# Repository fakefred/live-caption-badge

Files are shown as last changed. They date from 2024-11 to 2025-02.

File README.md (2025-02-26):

# Live Caption Badge

The Live Caption Badge is my team's capstone project for EECS 473, from
September to December 2024. It is a device that transmits and transcribes
speech in a noisy environment in real-time for the hard of hearing.

For technical details, please read [our report](report.pdf) (10.6 MiB).

## Technical Highlights

- ESP32 with ESP-IDF and ESP-ADF
- FreeRTOS
- Audio streaming over HTTP
- Peer discovery over BLE
- Real-time speech-to-text with Vosk
- E-Paper over SPI
- Audio over I2S

## Files

- `firmware` is the firmware our product actually ran on Design Expo.
- `audio`, `BLEnWifi`, `echo`, `epaper` contain the code we used to test
  various components.
- `pcb` is our PCB design. It is a 4-layer board.
- `transcribe` contains the code for the central server `server_esp.py`,
  which ran on a laptop on Design Expo. It is responsible for transcribing
  text and relaying audio. We also used `hack.py` to apply hotfixes to the
  badges.

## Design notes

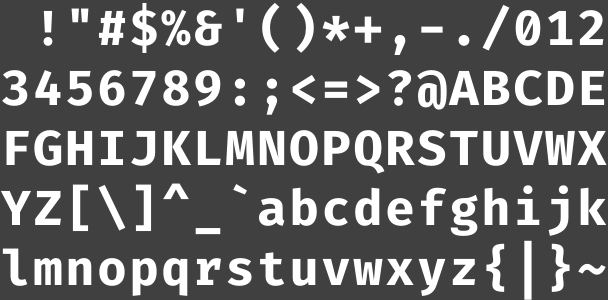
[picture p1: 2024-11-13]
epaper/tools/firacode48.png

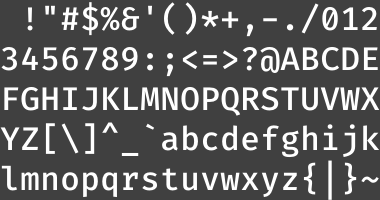
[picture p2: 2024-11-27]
epaper/tools/firacode32.png

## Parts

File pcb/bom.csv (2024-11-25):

Reference | Value | Qty
BT1 |  | 1
C1 | 100uF | 1
C2 | 22uF | 1
C3,C14,C15,C33,C34,C35 | 0.1uF | 6
C4,C5,C11-C13,C16-C21,C24-C32,C38-C40,C45 | 1uF | 24
C6 | 47uF | 1
C7-C10,C37,C41-C44,C46 | 10uF | 10
C22,C23,C48 | 22pF | 3
C36 | NC | 1
C47 | 4.7uF | 1
D1 | LED | 1
D2,D3,D4 | MBR0530 | 3
J1 | FPC24 | 1
J2 | Conn_01x06 | 1
J4 | AudioJack4 | 1
J5 | USB_C_Receptacle_USB2.0_16P | 1
L1 | 68uH | 1
Q1 | Si1308EDL | 1
Q2,Q3 | SS8050 | 2
R1,R7,R18,R19 | 10k | 4
R2,R3 | 3.3k | 2
R4,R5,R6 | 5.1k | 3
R8,R13,R14 | 0 | 3
R9 | 51 | 1
R10 | 2.2k | 1
R11,R12,R15 | 150k | 3
R16 | 300k | 1
R17 | 0.47 | 1
SW1 | SW_DPDT_x2 | 1
SW2 | RST | 1
SW3,SW4,SW5 | BTN | 3
SW6 | FLASH | 1
TP1-TP17 | TestPoint | 17
U1 | ESP32-S3-WROOM-1 | 1
U2,U3 | HE9073A33M5R | 2
U4 | ES7210 | 1
U5 | ES8311 | 1
U6 | IS31AP2005 | 1

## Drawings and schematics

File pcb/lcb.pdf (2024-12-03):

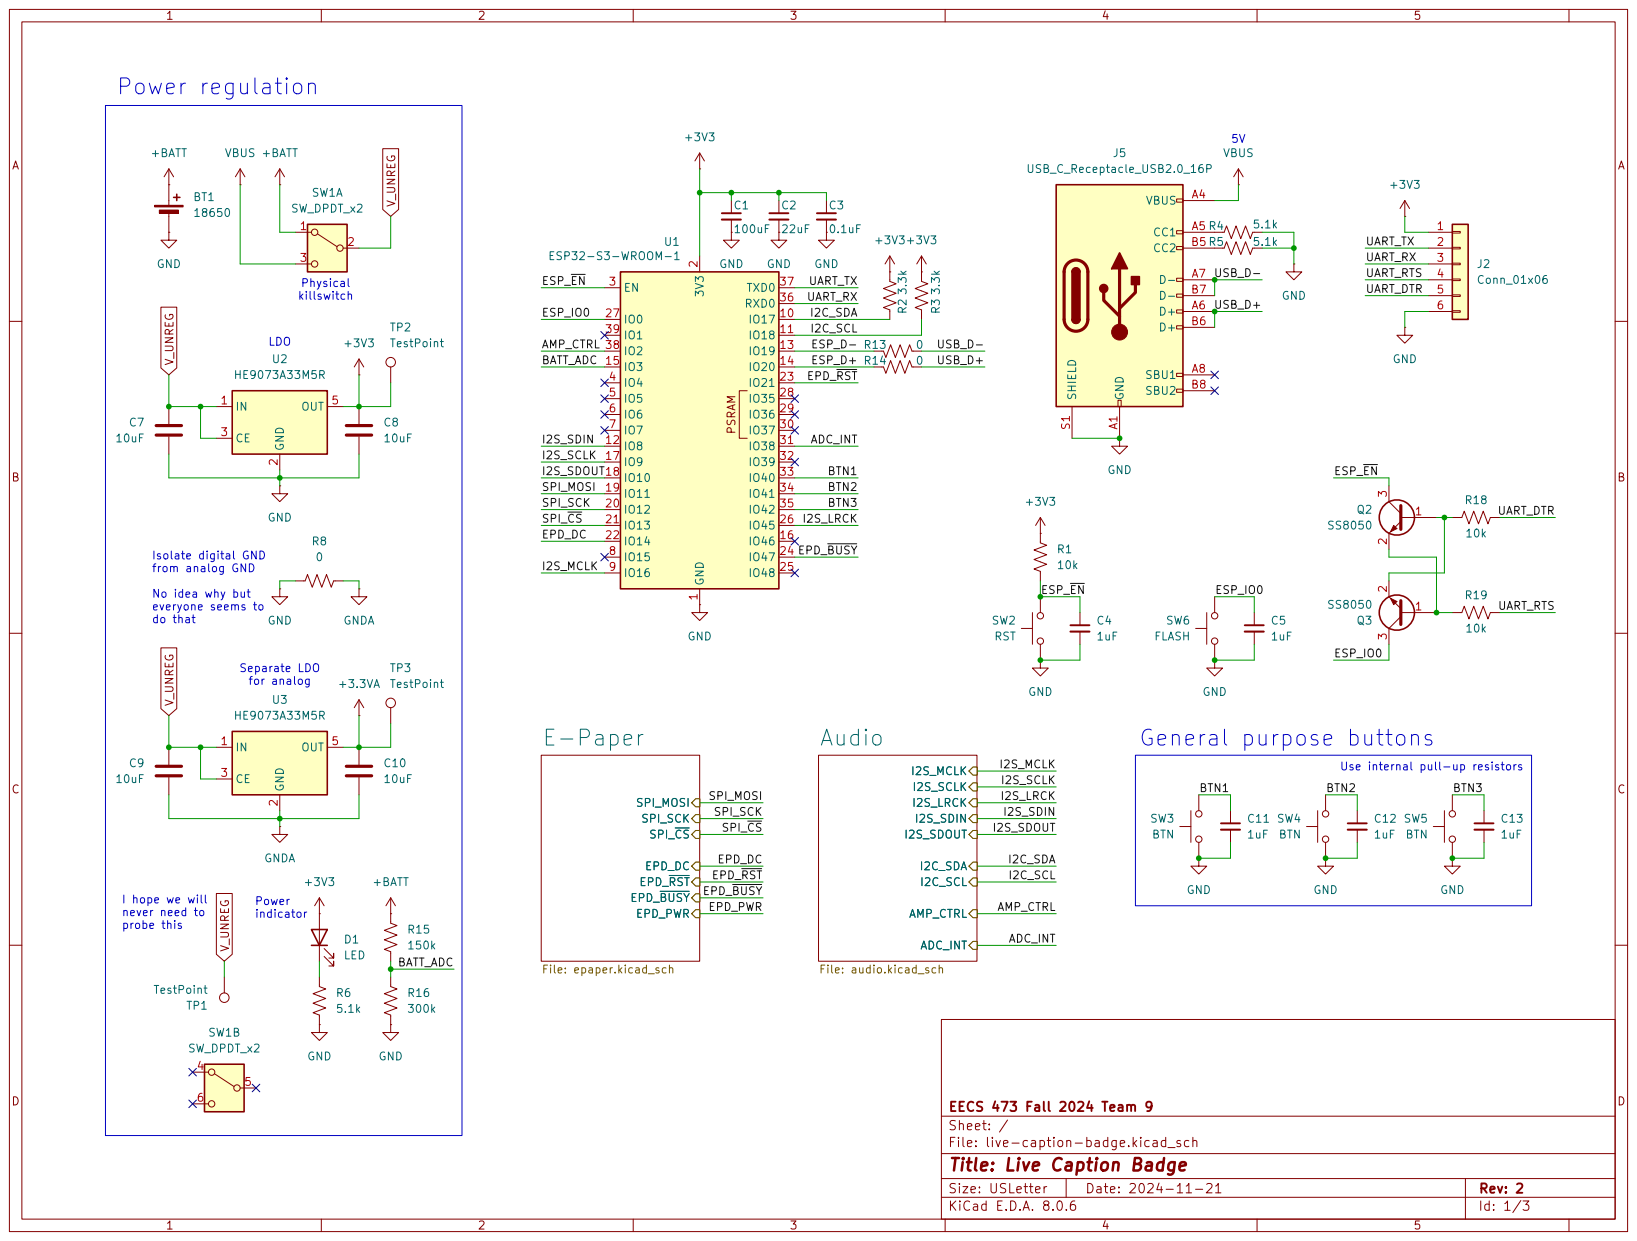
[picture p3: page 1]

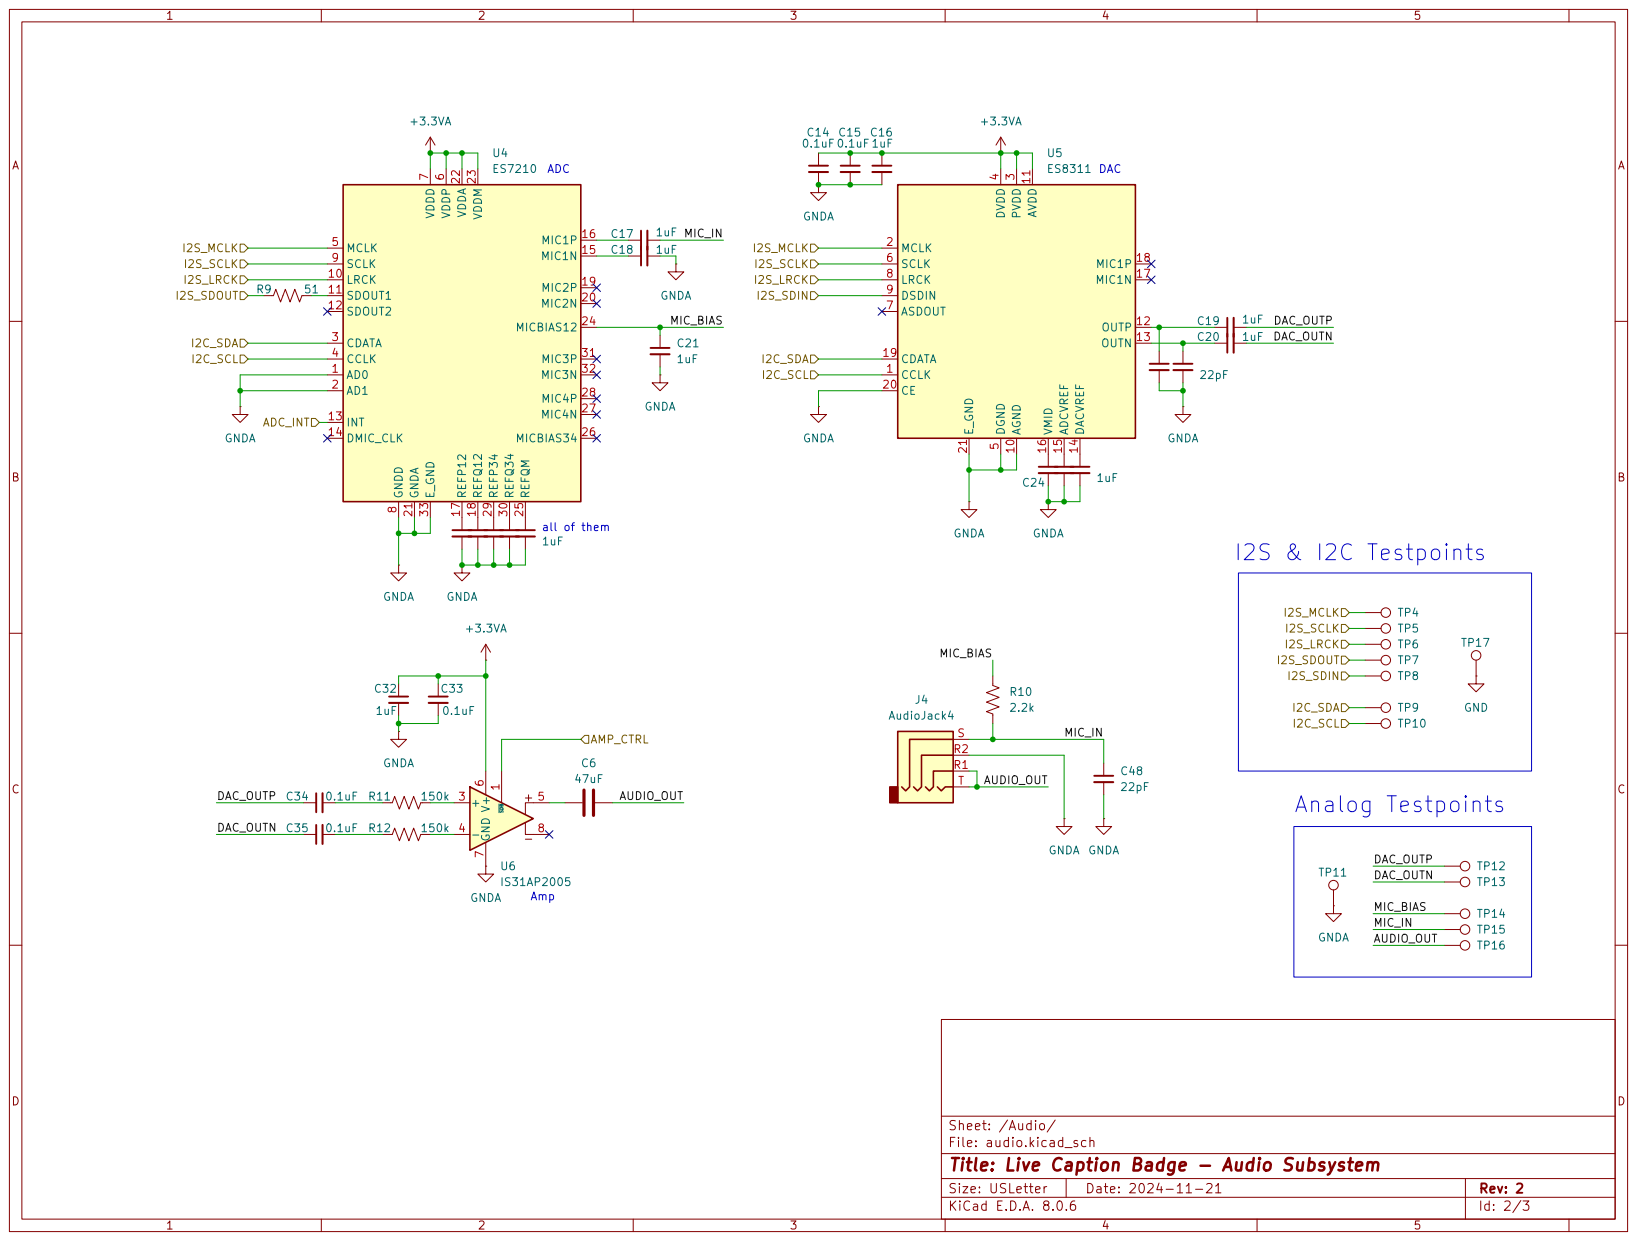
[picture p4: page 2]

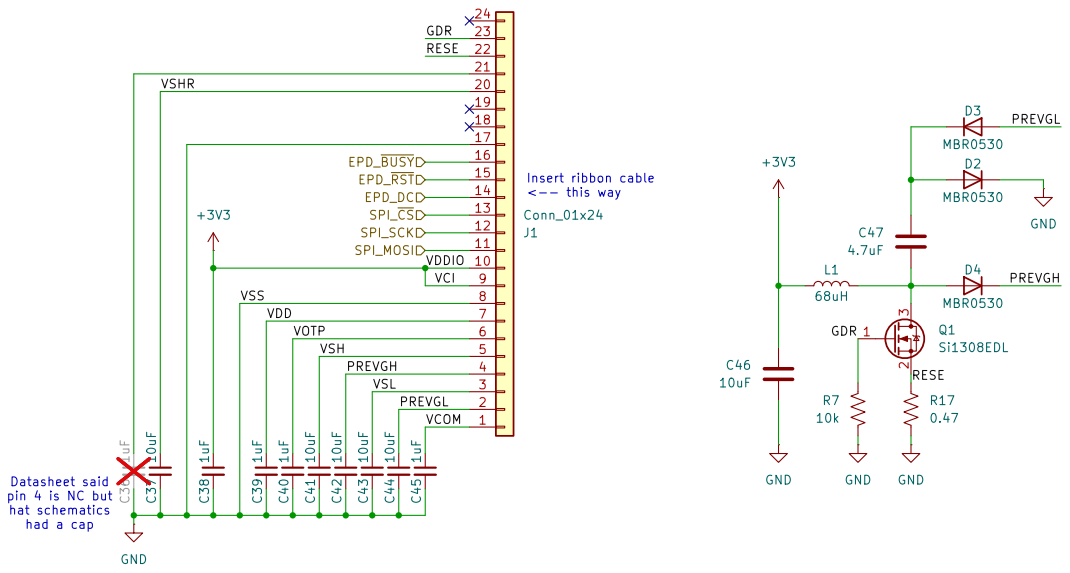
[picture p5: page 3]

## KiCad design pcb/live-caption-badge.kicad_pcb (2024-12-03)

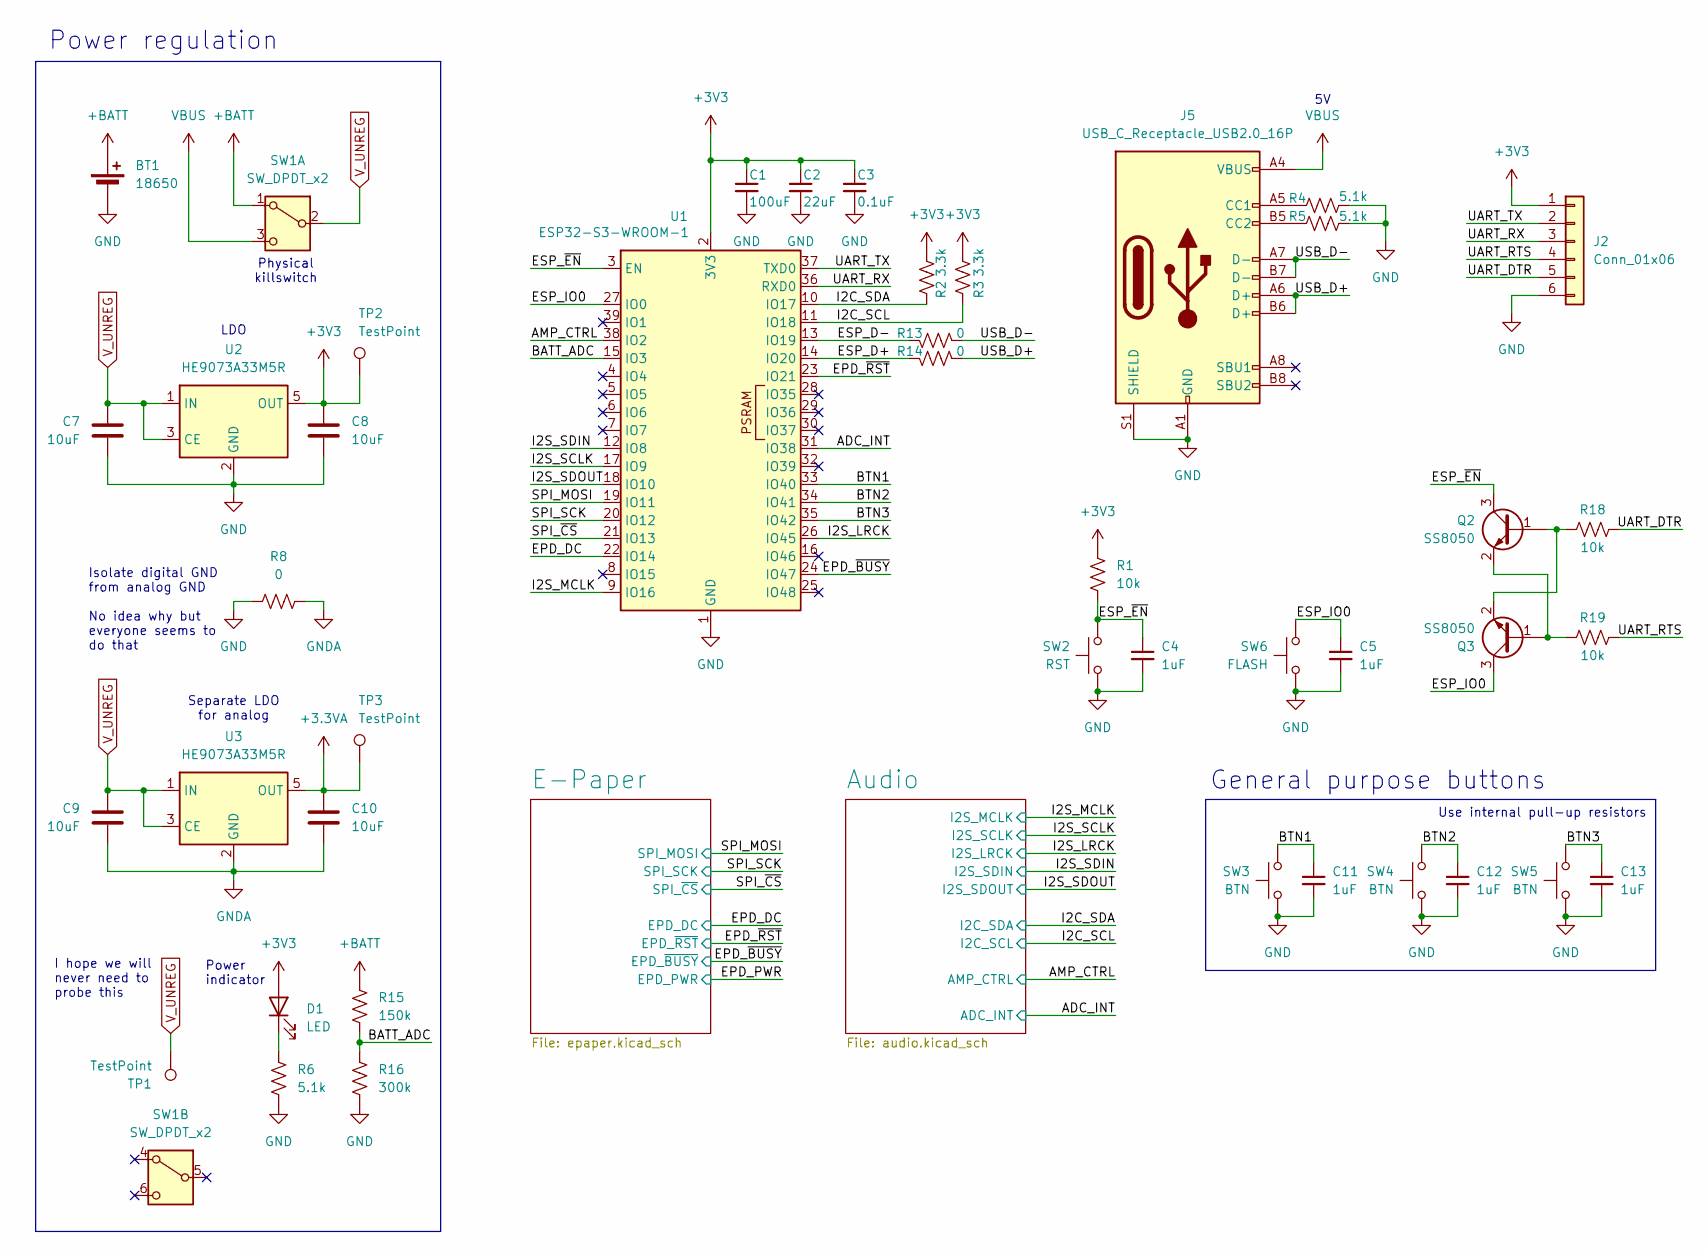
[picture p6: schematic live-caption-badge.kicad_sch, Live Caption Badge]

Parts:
BT1: 18650; BH-18650-B1BA002
C1: 100uF; CP_Radial_D8.0mm_P3.50mm
C2: 22uF; C_0603_1608Metric
C3: 0.1uF; C_0603_1608Metric
C4, C5, C11, C12, C13: 1uF; C_0603_1608Metric
C7, C8, C9, C10: 10uF; C_0603_1608Metric
D1: LED; LED_0603_1608Metric
J2: Conn_01x06; PinHeader_1x06_P2.54mm_Vertical
J5: USB_C_Receptacle_USB2.0_16P; USB_C_Receptacle_Molex_2169900002
Q2, Q3: SS8050; SOT-23
R1, R18, R19: 10k; R_0603_1608Metric
R2, R3: 3.3k; R_0603_1608Metric
R4, R5, R6: 5.1k; R_0603_1608Metric
R8, R13, R14: 0; R_0603_1608Metric
R15: 150k; R_0603_1608Metric
R16: 300k; R_0603_1608Metric
SW1: SW_DPDT_x2; SW_DPDT_SLW-867569-4A-N-D
SW2: RST; SW_Push_6x3mm
SW3, SW4, SW5: BTN; SW_Push_TL1100CF160Q
SW6: FLASH; SW_Push_6x3mm
TP1, TP2, TP3: TestPoint; PinHeader_1x01_P2.54mm_Vertical
U1: ESP32-S3-WROOM-1; ESP32-S3-WROOM-1-LargerVias
U2, U3: HE9073A33M5R; SOT-23-5

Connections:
+3.3VA: C10.1, TP3.1, U3.5 (OUT); also elsewhere on the board
+3V3: C1.1, C2.1, C3.1, C8.1, D1.2 (A), J2.1, R1.1, R2.1, R3.1, TP2.1, U1.2 (3V3), U2.5 (OUT); also elsewhere on the board
+BATT: BT1.1 (+), R15.2, SW1.1 (A)
/ADC_INT: U1.31 (IO38); also elsewhere on the board
/AMP_CTRL: U1.38 (IO2); also elsewhere on the board
/BATT_ADC: R15.1, R16.2, U1.15 (IO3)
/BTN1: C11.1, SW3.2, U1.33 (IO40)
/BTN2: C12.1, SW4.2, U1.34 (IO41)
/BTN3: C13.1, SW5.2, U1.35 (IO42)
/EPD_DC: U1.22 (IO14); also elsewhere on the board
/EPD_~BUSY: U1.24 (IO47); also elsewhere on the board
/EPD_~RST: U1.23 (IO21); also elsewhere on the board
/ESP_D+: R14.2, U1.14 (IO20)
/ESP_D-: R13.2, U1.13 (IO19)
/ESP_IO0: C5.1, Q3.3 (C), SW6.2, U1.27 (IO0)
/ESP_~EN: C4.1, Q2.3 (C), R1.2, SW2.2, U1.3 (EN)
/I2C_SCL: R3.2, U1.11 (IO18); also elsewhere on the board
/I2C_SDA: R2.2, U1.10 (IO17); also elsewhere on the board
/I2S_LRCK: U1.26 (IO45); also elsewhere on the board
/I2S_MCLK: U1.9 (IO16); also elsewhere on the board
/I2S_SCLK: U1.17 (IO9); also elsewhere on the board
/I2S_SDIN: U1.12 (IO8); also elsewhere on the board
/I2S_SDOUT: U1.18 (IO10); also elsewhere on the board
/SPI_MOSI: U1.19 (IO11); also elsewhere on the board
/SPI_SCK: U1.20 (IO12); also elsewhere on the board
/SPI_~CS: U1.21 (IO13); also elsewhere on the board
/UART_DTR: J2.5, R18.2
/UART_RTS: J2.4, R19.2
/UART_RX: J2.3, U1.36 (RXD0)
/UART_TX: J2.2, U1.37 (TXD0)
/USB_D+: J5.A6 (D+), J5.B6 (D+), R14.1
/USB_D-: J5.A7 (D-), J5.B7 (D-), R13.1
GND: BT1.2 (-), C1.2, C2.2, C3.2, C4.2, C5.2, C7.2, C8.2, C11.2, C12.2, C13.2, J2.6, J5.A1 (GND), J5.A12 (GND), J5.B1 (GND), J5.B12 (GND), J5.S1 (SHIELD), R4.2, R5.2, R6.1, R8.1, R16.1, SW2.1, SW3.1, SW4.1, SW5.1, SW6.1, U1.1 (GND), U1.40 (GND), U1.41 (GND), U2.2 (GND); also elsewhere on the board
GNDA: C9.2, C10.2, R8.2, U3.2 (GND); also elsewhere on the board
unnamed: D1.1 (K), R6.2
unnamed: J5.A5 (CC1), R4.1
unnamed: J5.B5 (CC2), R5.1
unnamed: Q2.1 (B), Q3.2 (E), R18.1
unnamed: Q2.2 (E), Q3.1 (B), R19.1
VBUS: J5.A4 (VBUS), J5.A9 (VBUS), J5.B4 (VBUS), J5.B9 (VBUS), SW1.3 (C)
V_UNREG: C7.1, C9.1, SW1.2 (B), TP1.1, U2.1 (IN), U2.3 (CE), U3.1 (IN), U3.3 (CE)

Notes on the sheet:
Power regulation
Physical killswitch
LDO
I hope we will never need to probe this
Power indicator
Use internal pull-up resistors
General purpose buttons
Isolate digital GND from analog GND No idea why but everyone seems to do that
Separate LDO for analog

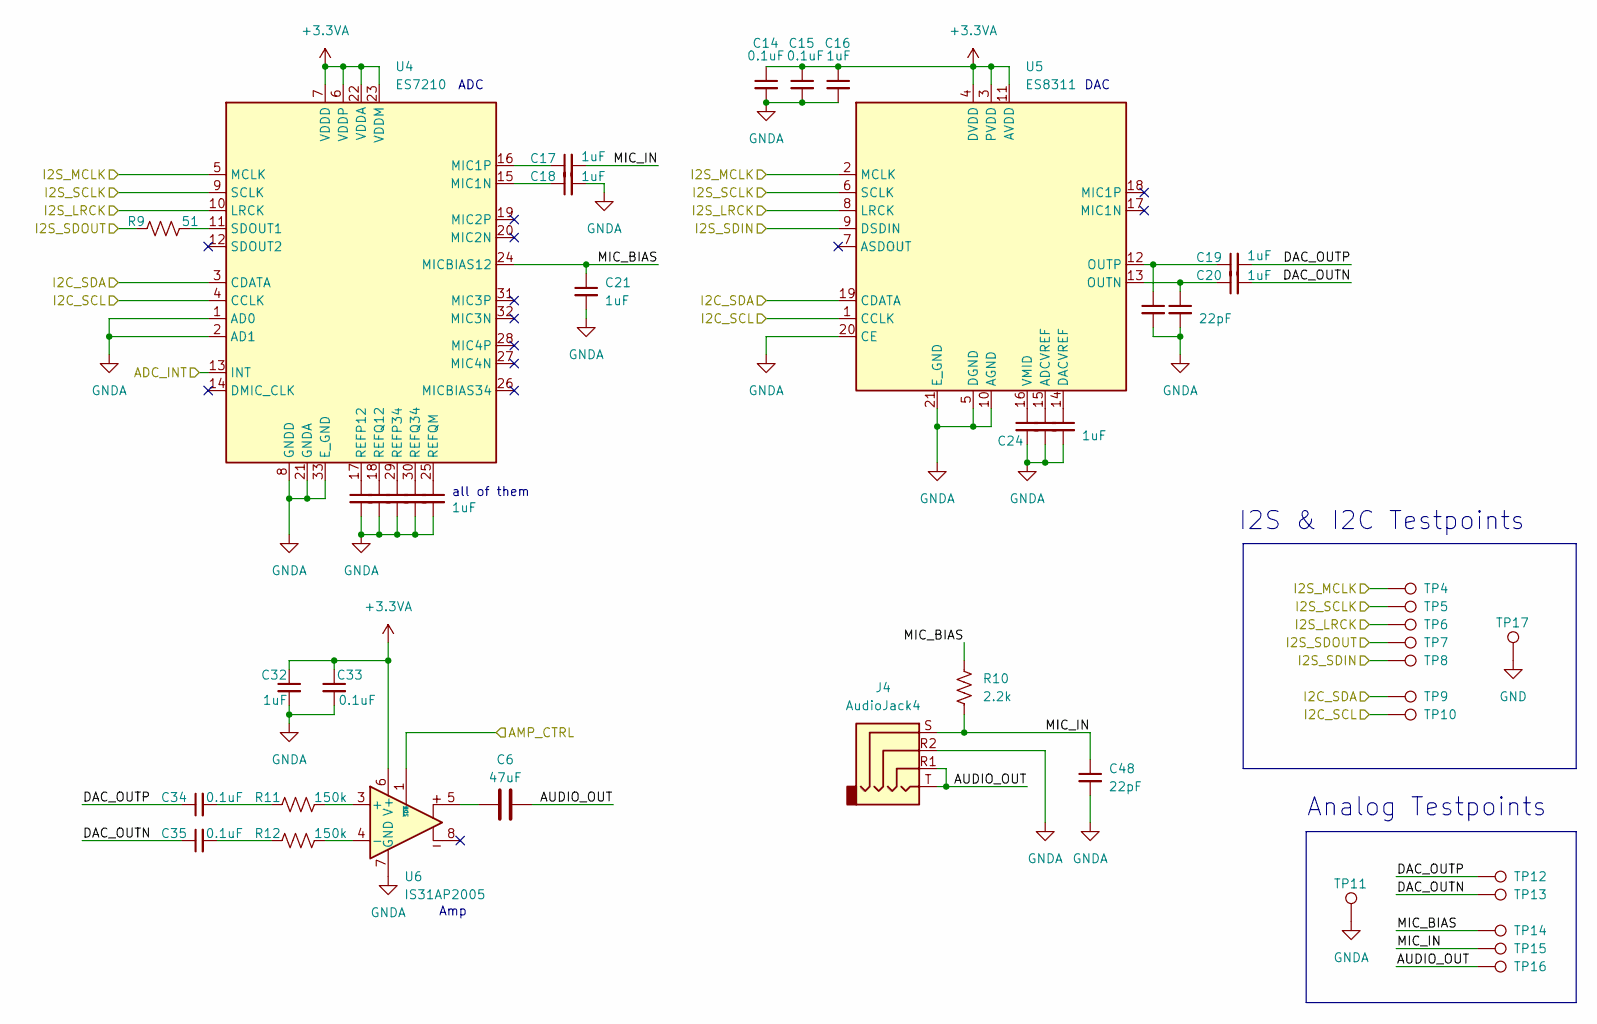
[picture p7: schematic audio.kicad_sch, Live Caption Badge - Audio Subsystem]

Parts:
C6: 47uF; C_0603_1608Metric
C14, C15, C33, C34, C35: 0.1uF; C_0603_1608Metric
C16, C17, C18, C19, C20, C21, C24, C25, C26, C27, C28, C29, C30, C31, C32: 1uF; C_0603_1608Metric
C22, C23, C48: 22pF; C_0603_1608Metric
J4: AudioJack4; Jack_3.5mm_PJ320D_Horizontal
R9: 51; R_0603_1608Metric
R10: 2.2k; R_0603_1608Metric
R11, R12: 150k; R_0603_1608Metric
TP4, TP5, TP6, TP7, TP8, TP9, TP10, TP11, TP12, TP13, TP14, TP15, TP16, TP17: TestPoint; PinHeader_1x01_P2.54mm_Vertical
U4: ES7210; QFN-32-1EP_4x4mm_P0.4mm_EP2.9x2.9mm
U5: ES8311; QFN-20-1EP_3x3mm_P0.4mm_EP1.65x1.65mm
U6: IS31AP2005; MSOP-8_3x3mm_P0.65mm

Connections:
+3.3VA: C14.1, C15.1, C16.1, C32.1, C33.1, U4.6 (VDDP), U4.7 (VDDD), U4.22 (VDDA), U4.23 (VDDM), U5.3 (PVDD), U5.4 (DVDD), U5.11 (AVDD), U6.6 (V+); also elsewhere on the board
/ADC_INT: U4.13 (INT); also elsewhere on the board
/AMP_CTRL: U6.1 (~SDB); also elsewhere on the board
/Audio/AUDIO_OUT: C6.2, J4.R1, J4.T, TP16.1
/Audio/DAC_OUTN: C20.2, C35.1, TP13.1
/Audio/DAC_OUTP: C19.2, C34.1, TP12.1
/Audio/MIC_BIAS: C21.1, R10.1, TP14.1, U4.24 (MICBIAS12)
/Audio/MIC_IN: C17.2, C48.1, J4.S, R10.2, TP15.1
/I2C_SCL: TP10.1, U4.4 (CCLK), U5.1 (CCLK); also elsewhere on the board
/I2C_SDA: TP9.1, U4.3 (CDATA), U5.19 (CDATA); also elsewhere on the board
/I2S_LRCK: TP6.1, U4.10 (LRCK), U5.8 (LRCK); also elsewhere on the board
/I2S_MCLK: TP4.1, U4.5 (MCLK), U5.2 (MCLK); also elsewhere on the board
/I2S_SCLK: TP5.1, U4.9 (SCLK), U5.6 (SCLK); also elsewhere on the board
/I2S_SDIN: TP8.1, U5.9 (DSDIN); also elsewhere on the board
/I2S_SDOUT: R9.1, TP7.1; also elsewhere on the board
GND: TP17.1; also elsewhere on the board
GNDA: C14.2, C15.2, C16.2, C18.2, C21.2, C22.2, C23.2, C24.2, C25.2, C26.2, C27.2, C28.2, C29.2, C30.2, C31.2, C32.2, C33.2, C48.2, J4.R2, TP11.1, U4.1 (AD0), U4.2 (AD1), U4.8 (GNDD), U4.21 (GNDA), U4.33 (E_GND), U5.5 (DGND), U5.10 (AGND), U5.20 (CE), U5.21 (E_GND), U6.7 (GND); also elsewhere on the board
unnamed: C6.1, U6.5
unnamed: C34.2, R11.1
unnamed: C35.2, R12.1
unnamed: C18.1, U4.15 (MIC1N)
unnamed: C17.1, U4.16 (MIC1P)
unnamed: C27.1, U4.17 (REFP12)
unnamed: C29.1, U4.29 (REFP34)
unnamed: C28.1, U4.18 (REFQ12)
unnamed: C30.1, U4.30 (REFQ34)
unnamed: C31.1, U4.25 (REFQM)
unnamed: R9.2, U4.11 (SDOUT1)
unnamed: C25.1, U5.15 (ADCVREF)
unnamed: C26.1, U5.14 (DACVREF)
unnamed: C20.1, C23.1, U5.13 (OUTN)
unnamed: C19.1, C22.1, U5.12 (OUTP)
unnamed: C24.1, U5.16 (VMID)
unnamed: R11.2, U6.3 (+)
unnamed: R12.2, U6.4 (-)

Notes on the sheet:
DAC
all of them
Amp
Analog Testpoints
I2S & I2C Testpoints
ADC

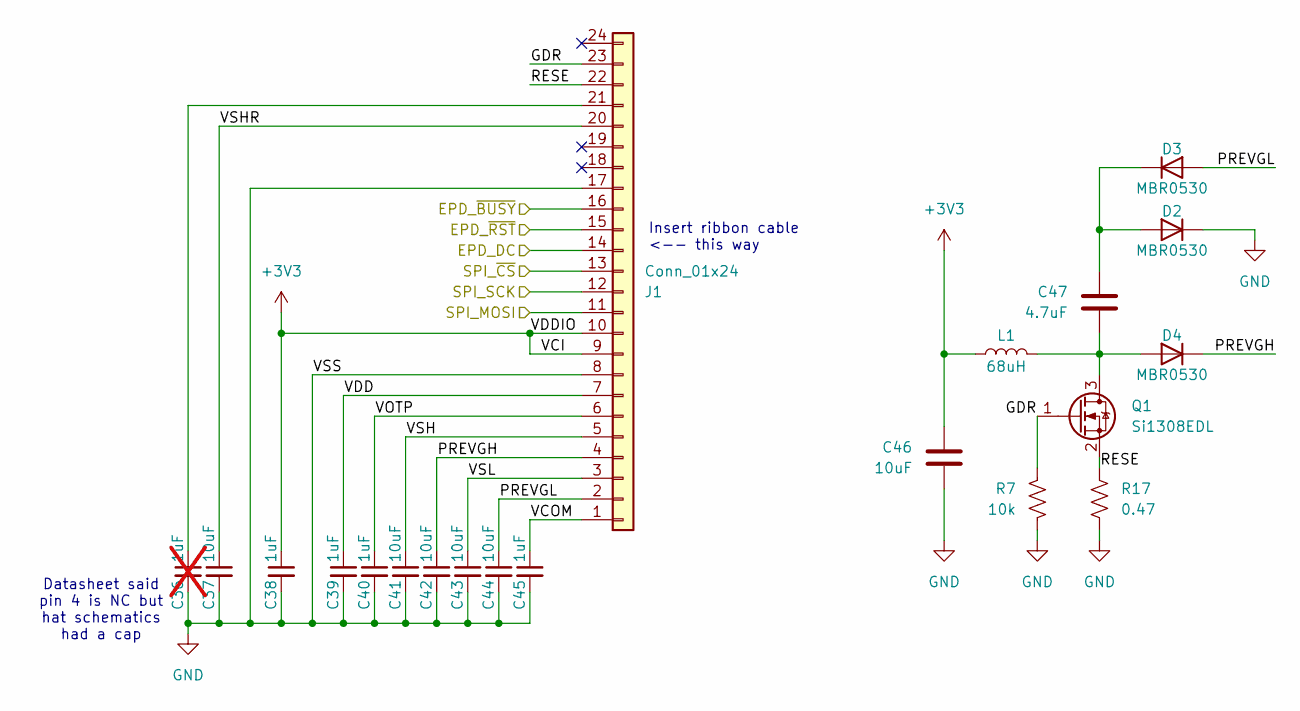
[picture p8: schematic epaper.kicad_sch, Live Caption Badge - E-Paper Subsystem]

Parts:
C36: 1uF; C_0603_1608Metric; not fitted
C37, C41, C42, C43, C44, C46: 10uF; C_0603_1608Metric
C38, C39, C40, C45: 1uF; C_0603_1608Metric
C47: 4.7uF; C_0603_1608Metric
D2, D3, D4: MBR0530; D_SOD-123
J1: Conn_01x24; FPC05024-13200_1x24-1MP_P0.50_Horizontal
L1: 68uH; L_Bourns-SDEE0406A
Q1: Si1308EDL; SOT-323_SC-70
R7: 10k; R_0603_1608Metric
R17: 0.47; R_0603_1608Metric

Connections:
+3V3: C38.1, C46.1, J1.9, J1.10, L1.1; also elsewhere on the board
/E-Paper/GDR: J1.23, Q1.1 (G), R7.1
/E-Paper/PREVGH: C42.1, D4.1 (K), J1.4
/E-Paper/PREVGL: C44.1, D3.2 (A), J1.2
/E-Paper/RESE: J1.22, Q1.2 (S), R17.1
/E-Paper/VCOM: C45.1, J1.1
/E-Paper/VDD: C39.1, J1.7
/E-Paper/VOTP: C40.1, J1.6
/E-Paper/VSH: C41.1, J1.5
/E-Paper/VSHR: C37.1, J1.20
/E-Paper/VSL: C43.1, J1.3
/EPD_DC: J1.14; also elsewhere on the board
/EPD_~BUSY: J1.16; also elsewhere on the board
/EPD_~RST: J1.15; also elsewhere on the board
/SPI_MOSI: J1.11; also elsewhere on the board
/SPI_SCK: J1.12; also elsewhere on the board
/SPI_~CS: J1.13; also elsewhere on the board
GND: C36.2, C37.2, C38.2, C39.2, C40.2, C41.2, C42.2, C43.2, C44.2, C45.2, C46.2, D2.1 (K), J1.8, J1.17, R7.2, R17.2; also elsewhere on the board
unnamed: C47.1, D2.2 (A), D3.1 (K)
unnamed: C47.2, D4.2 (A), L1.2, Q1.3 (D)
unnamed: C36.1, J1.21

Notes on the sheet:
Datasheet said pin 4 is NC but hat schematics had a cap
Insert ribbon cable <-- this way

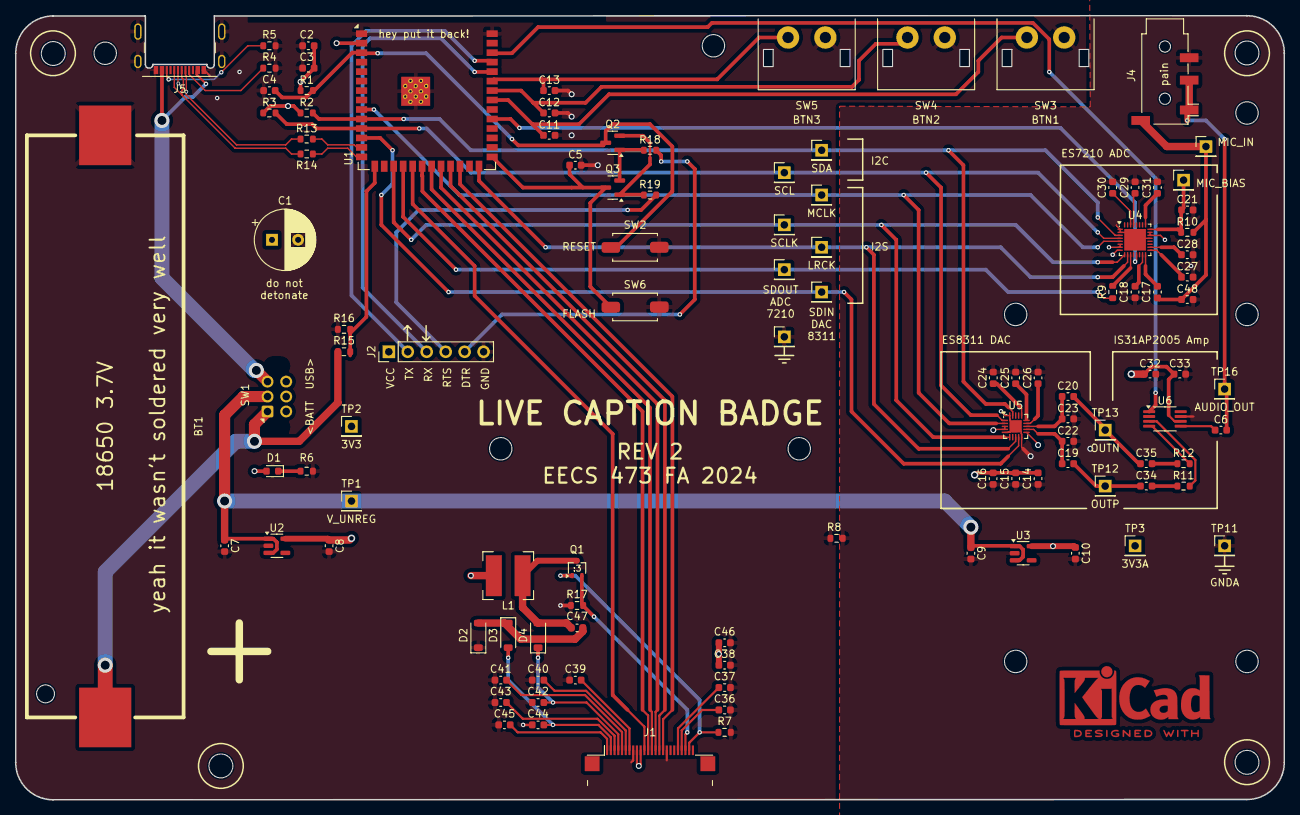
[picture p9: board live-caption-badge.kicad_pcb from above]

Board: 4 copper layers, 170.0 x 105.1 mm, 109 parts (0 on the bottom side), 77 nets.

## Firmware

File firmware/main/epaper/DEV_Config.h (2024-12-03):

/*****************************************************************************
* | File      	:   DEV_Config.h
* | Author      :   Waveshare team
* | Function    :   Hardware underlying interface
* | Info        :
*----------------
* |	This version:   V1.0
* | Date        :   2020-02-19
* | Info        :
#
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
******************************************************************************/
#ifndef _DEV_CONFIG_H_
#define _DEV_CONFIG_H_

#include "driver/gpio.h"
#include "freertos/FreeRTOS.h"
#include "SPI.h"
#include <stdint.h>
#include <stdio.h>

/**
 * data
 **/
#define UBYTE uint8_t
#define UWORD uint16_t
#define UDOUBLE uint32_t

/**
 * GPIO config
 **/
#define EPD_SCK_PIN GPIO_NUM_12
#define EPD_MOSI_PIN GPIO_NUM_11
#define EPD_MISO_PIN GPIO_NUM_48 // unused
#define EPD_CS_PIN GPIO_NUM_13
#define EPD_RST_PIN GPIO_NUM_21
#define EPD_DC_PIN GPIO_NUM_14
#define EPD_BUSY_PIN GPIO_NUM_47
#define EPD_PWR_PIN GPIO_NUM_7

#define GPIO_PIN_SET 1
#define GPIO_PIN_RESET 0

#define HIGH 1
#define LOW 0

/**
 * GPIO read and write
 **/
#define DEV_Digital_Write(_pin, _value) gpio_set_level(_pin, _value)
#define DEV_Digital_Read(_pin) gpio_get_level(_pin)

/**
 * delay x ms
 **/
#define DEV_Delay_ms(__xms) vTaskDelay(pdMS_TO_TICKS(__xms))

/*------------------------------------------------------------------------------------------------------*/
UBYTE DEV_Module_Init(void);
void  GPIO_Mode(UWORD GPIO_Pin, UWORD Mode);
void  DEV_SPI_WriteByte(UBYTE data);
UBYTE DEV_SPI_ReadByte();
void  DEV_SPI_Write_nByte(UBYTE *pData, UDOUBLE len);

#endif

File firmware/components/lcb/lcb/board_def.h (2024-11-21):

/*
 * ESPRESSIF MIT License
 *
 * Copyright (c) 2020 <ESPRESSIF SYSTEMS (SHANGHAI) CO., LTD>
 *
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
 */

#ifndef _AUDIO_BOARD_DEFINITION_H_
#define _AUDIO_BOARD_DEFINITION_H_

#include "audio_hal.h"

#define SDCARD_OPEN_FILE_NUM_MAX  5

#define BOARD_PA_GAIN             (10) /* Power amplifier gain defined by board (dB) */

#define SDCARD_PWR_CTRL             -1
#define ESP_SD_PIN_CLK              -1
#define ESP_SD_PIN_CMD              -1
#define ESP_SD_PIN_D0               -1
#define ESP_SD_PIN_D1               -1
#define ESP_SD_PIN_D2               -1
#define ESP_SD_PIN_D3               -1
#define ESP_SD_PIN_D4               -1
#define ESP_SD_PIN_D5               -1
#define ESP_SD_PIN_D6               -1
#define ESP_SD_PIN_D7               -1
#define ESP_SD_PIN_CD               -1
#define ESP_SD_PIN_WP               -1

#define INPUT_KEY_USER_ID_1 42
#define INPUT_KEY_USER_ID_2 41
#define INPUT_KEY_USER_ID_3 40

#define BUTTON_ID_1 42
#define BUTTON_ID_2 41
#define BUTTON_ID_3 40

extern audio_hal_func_t AUDIO_CODEC_ES7210_DEFAULT_HANDLE;
extern audio_hal_func_t AUDIO_CODEC_ES8311_DEFAULT_HANDLE;

#define AUDIO_CODEC_DEFAULT_CONFIG()                                           \
	{                                                                      \
	    .adc_input = AUDIO_HAL_ADC_INPUT_LINE1,                            \
	    .dac_output = AUDIO_HAL_DAC_OUTPUT_ALL,                            \
	    .codec_mode = AUDIO_HAL_CODEC_MODE_BOTH,                           \
	    .i2s_iface =                                                       \
	        {                                                              \
	            .mode = AUDIO_HAL_MODE_SLAVE,                              \
	            .fmt = AUDIO_HAL_I2S_NORMAL,                               \
	            .samples = AUDIO_HAL_16K_SAMPLES,                          \
	            .bits = AUDIO_HAL_BIT_LENGTH_16BITS,                       \
	        },                                                             \
	};

#define INPUT_KEY_NUM     3             /* You need to define the number of input buttons on your board */

#define INPUT_KEY_DEFAULT_INFO()                                               \
	{                                                                      \
	    {                                                                  \
	        .type = PERIPH_ID_BTN,                                         \
	        .user_id = INPUT_KEY_USER_ID_1,                                \
	        .act_id = BUTTON_ID_1,                                         \
	    },                                                                 \
	    {                                                                  \
	        .type = PERIPH_ID_BTN,                                         \
	        .user_id = INPUT_KEY_USER_ID_2,                                \
	        .act_id = BUTTON_ID_2,                                         \
	    },                                                                 \
	    {                                                                  \
	        .type = PERIPH_ID_BTN,                                         \
	        .user_id = INPUT_KEY_USER_ID_3,                                \
	        .act_id = BUTTON_ID_3,                                         \
	    },                                                                 \
	}

#endif

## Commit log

2024-10-23 pcb: Add ES7210
    [live-caption-badge.kicad_sch]
2024-10-23 pcb: moved things around
    [audio.kicad_sch, live-caption-badge.kicad_sch]
2024-10-23 epaper driver schematic
    [epaper_driver.kicad_sch, live-caption-badge.kicad_sch]
2024-10-23 pcb: Add ES8311
    [audio.kicad_sch]
2024-10-26 pcb: Audio subschematic seems done
    [audio.kicad_sch, live-caption-badge.kicad_sch]
2024-10-27 pcb: Schematics seem complete
    [epaper_driver.kicad_sch, live-caption-badge.kicad_sch]
2024-10-27 pcb: Renumber parts
    [audio.kicad_sch, live-caption-badge.kicad_sch]
2024-10-27 pcb: Assigned footprints (the more trivial ones)
    [audio.kicad_sch, live-caption-badge.kicad_sch]
2024-10-28 pcb: Begin layout
    [live-caption-badge.kicad_pcb, live-caption-badge.kicad_sch]
2024-10-28 pcb: More layout, design 18650 battery holder footprint
    [live-caption-badge.kicad_pcb, live-caption-badge.kicad_sch]
2024-10-29 pcb: I'm working in Spain but the S is silent
    [audio.kicad_sch, live-caption-badge.kicad_pcb, live-caption-badge.kicad_sch]
2024-10-30 pcb: 473 cannot defeat me in any way that matters
    [audio.kicad_sch, live-caption-badge.kicad_pcb, live-caption-badge.kicad_sch]
2024-10-30 pcb: pretty much done
    [live-caption-badge.kicad_pcb, live-caption-badge.kicad_sch]
2024-10-30 pcb: Fix misc footprints, add silkprint
    [audio.kicad_sch, live-caption-badge.kicad_pcb, live-caption-badge.kicad_sch]
2024-10-30 pcb: Checkpoint before incorporating Mark and James' suggestions
    [audio.kicad_sch, live-caption-badge.kicad_pcb, live-caption-badge.kicad_sch]
2024-10-30 pcb: Convert to 4-layer board
    [audio.kicad_sch, live-caption-badge.kicad_pcb, live-caption-badge.kicad_sch]
2024-10-31 pcb: it may or may not work
    [audio.kicad_sch, live-caption-badge.kicad_pcb, live-caption-badge.kicad_sch]
2024-10-31 pcb: Yippee
    [live-caption-badge.kicad_pcb, live-caption-badge.kicad_sch]
2024-10-31 pcb: Slap a KiCad logo on it
    [live-caption-badge.kicad_pcb]
2024-10-31 pcb: Rev 1 Gerbers
    [live-caption-badge-B_Cu.gbr, live-caption-badge-B_Mask.gbr, live-caption-badge-B_Paste.gbr, live-caption-badge-B_Silkscreen.gbr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]
2024-10-31 pcb: Edit a couple R/C values, generate BOM
    [bom.ods, live-caption-badge.kicad_pcb, live-caption-badge.kicad_sch]
2024-11-05 modify reading frame part to handle the data, should work and pending sending suitable response.
2024-11-06 epaper: Port Arduino driver to esp-idf
2024-11-13 Add a task to periodically send GET request to retreive transcribed result, and another task to print the current content of the buffer.
2024-11-14 epaper: Unify pin assignments in DEV_Config.h and SPI.h
2024-11-14 epaper: EPD_7IN5_V2_Display_Part now reads from full-screen framebuffer
2024-11-14 epaper: Allow printing caption anywhere on screen
2024-11-20 epaper: Port to PCB
2024-11-20 epaper: PCB pin assignments
2024-11-22 pcb: Rev 2 schematic
    [audio.kicad_sch, bom.ods, epaper.kicad_sch, live-caption-badge.kicad_pcb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]
2024-11-23 pcb: rev 2?
    [audio.kicad_sch, epaper.kicad_sch, live-caption-badge.kicad_pcb, live-caption-badge.kicad_sch]
2024-11-24 pcb: Flip FPC, 170x105mm
    [epaper.kicad_sch, live-caption-badge.kicad_pcb, live-caption-badge.kicad_sch]
2024-11-24 pcb: move stuff
    [live-caption-badge.kicad_pcb]
2024-11-25 pcb: rev 2 ready?
    [audio.kicad_sch, epaper.kicad_sch, live-caption-badge.kicad_pcb, live-caption-badge.kicad_sch]
2024-11-25 pcb: Rev 2 gerbers
    [bom.csv, bom.ods, live-caption-badge-B_Cu.gbr, live-caption-badge-B_Mask.gbr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]
2024-11-27 update server for threading, upload Blue & WiFi C file for code refactoring.
2024-12-02 the server now transmitts the transcribed partial results to the board.
2024-12-03 pcb: Change paper size to US Letter
    [audio.kicad_sch, epaper.kicad_sch, live-caption-badge.kicad_pcb, live-caption-badge.kicad_sch]
2024-12-03 firmware: Unify everything we have
    [partitions.csv]
2024-12-09 transcribe: hack
    [dashboard.csv]
